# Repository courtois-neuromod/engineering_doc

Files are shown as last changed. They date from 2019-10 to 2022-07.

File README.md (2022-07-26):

# About
This document describes how to build the MR compatible videogame controller developed for the [Courtois Neuromod project](https://www.cneuromod.ca).

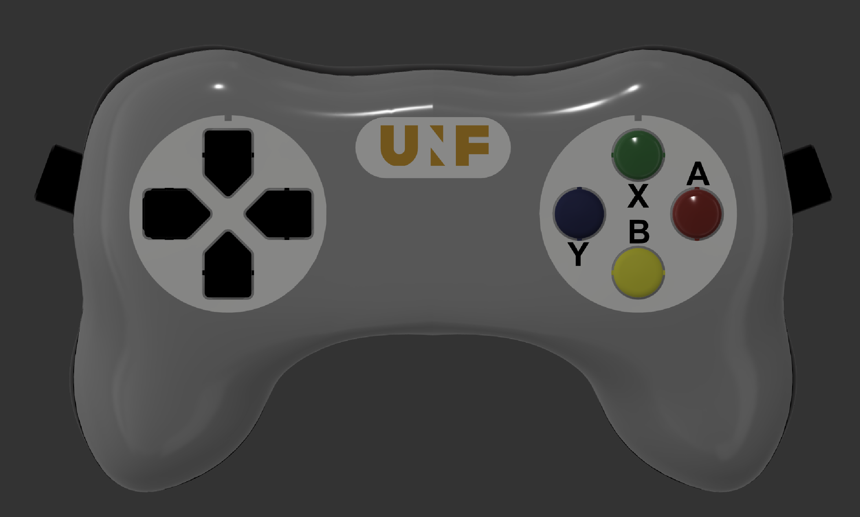
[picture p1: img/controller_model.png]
<br>
3D model of the controller design.

/!\ To add : overview schema of the different controller parts (i.e. body, fibers, PCB, stim computer)

## Documentation

- [Controller body assembly](https://github.com/courtois-neuromod/engineering_doc/blob/master/game_controller/controller_body/readme.md)
- [PCB electronics board](https://github.com/courtois-neuromod/engineering_doc/blob/master/game_controller/PCB/readme.md)
- [Software](https://github.com/courtois-neuromod/engineering_doc/tree/master/game_controller/teensy/source/readme.md)

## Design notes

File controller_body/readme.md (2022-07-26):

# Controller body instructions
This document describes the steps necessary to build and assemble the hand-held controller body part.

## Getting the parts
Aside from the 3D printed equipment and printed circuit boards, the parts required to build the controller can be obtained from two suppliers; [McMaster-Carr](http://mcmaster.com) and [Digikey](http://digikey.com). It is most likely possible to find other sources for the components, but the part numbers given here are for these two suppliers. The manufacturers names and part numbers are also given when available. The numbers given represent the bare minimum required to build the controller. Getting spares of everything is highly recommended.

## COTS
This section details the parts that need to be purchased directly from a supplier.
[BOM.md](BOM.md)

## Assembly

### Optical switches

#### Shutter assembly

Required:

Parts
  - Shutter_Blade x 8
  - Shutter_Cap x 8
  - Switch_Body x 8

Tools
  - Cyanoacrylate adhesive
  - Fine sanding paper or files
  - X-acto knife

Check both shutter blade and shutter cap for smoothness of surface and file or sand any rough surface. Test insertion of blade into slot at the bottom of shutter cap. It should slide to the bottom easily but you should still feel a bit of resistance. Put a drop of cyanoacrylate adhesive on a liquid tight surface, dip the end of shutter blade in adhesive and insert into slot at bottom of shutter cap.

Shutter assembly drawing | Shutter assembly exemple
---|---
Switch assembly exploded view |Switch assembly exploded view

#### Switch assembly

1. Disassemble a discarded computer keyboard to recuperate the membrane making the rubber dome switches. Individually cut away the switch dome parts and remove centre of top surface using an x-acto knife.

Silicone membrane

2. Test assembly of shutter, membrane and switch body by inserting the shutter by inserting the shutter blade into the empty centre part of rubber dome, then into gap at the top of switch body. The shutter blade should completely occult the guide hole for the fiber optic when button is pressed down, but leave it free when in upward position. The distance between the bottom
 of the shutter cap and the top of switch body will determine the stroke length of the key. The smaller this distance, the more responsive the controls will be. The shutter should move freely up and down.

 Air Gap Visual Check

 Shutter up | Shutter pressed down
 ---|---
 Shutter up |Shutter down

 3. Since the rubber domes recuperated from computer keyboards will very likely vary in dimensions, it might be necessary to modify shutter cap and shutter blade dimensions. The file [Shutter_Assembly_Param.f3d](CAD/f3d/Shutter_Assembly_Param.f3d) contains these two parts in Autodesk Fusion 360 format. The design is parametric to facilitate modifications. To edit the parts, open the file in **Fusion 360**, go to Modify, then select change parameters and expand User Parameters. Changing the value of parameter *Shutter_Cap_Shaft_Length* will allow to adjust the stroke length, while changing *Shutter_Blade_L* will allow ensuring correct shutter operation. That part is also available in [.step](/CAD/stp/Shutter_Cap.step) format for import in other CAD programs.

Parameters edit in Fusion 360<br>

4. Ensure that the air gap and the fiber optic guide in the 3D printed switch bodies are free of any residual PLA or support material. Hold switch body in front of a light source and check along Z axis for the air gap, and along horizontal axis for the fiber optic guide.

### Controller body

1. For each control on the controller, cut one length of duplex fiber optic to desired length between controller and interface module + 150 mm
2. Split each length of fiber on its length to separate the 2 fibers on a distance of approx. 750 mm from one end, and 25 mm from second end
3. Label each fiber with the name of matching control. On the end where the fibers are split for the largest distance (controller end) place a label on each single fiber
4. On the controller side of the fibers, make two bundles of fibers. Place one fiber of eac78h control in either bundle.
5. For one of the two bundles, cut the fibers for the directional pad controls about 150 mm shorter than the ones for the buttons. Do the opposite with the other bundle. This will allow a cleaner layout of the fibers inside the casing.
6. Strip and polish fibers **(need procedure)**
7. Cut two 500 mm lengths of the 13 mm ID plastic hose and fix those on the ends of the Y splitter
8. Fix second end of plastic hoses to extrusions on part *Casing_Bottom*

Fiber_Sheath_Assembly

Fiber_Sheath_Assembly

9. For each control, place a *Switch_Body* in matching groove inside casing.

Switch_Body_Positioning

10. Insert the fiber optics into Y splitter and push gently until both fibers emerge inside of casing. The bundle where the buttons fibers are longer will go on the directional pad side. There will be one fiber for each control in each branch of the Y. Make sure that the length protruding inside the casing is enough to reach into the corresponding *Switch_Module* and allow to lay out cleanly inside casing.
11. For each control, glue both fibers in place **(Need glue specs)**
12. Optional: Depending on fit tightness of *Switch_Module* parts inside grooves, it is also possible to glue the module in place. If gluing modules in place, wait for glue on fibers to set before proceeding
13. Place one threaded Nylon insert in each mounting post of part *Casing_Top*. If inserts don't fit inside, re-drill hole using 1/4" (6.35 mm) bit. If inserts are loose, use a drop of cyanoacrylate adhesive

Threaded_Inserts<br>

14. Before starting assembly, test bottom and top parts of casing for fit. The two halves should fit together without any visible gap. Common area that might need post processing are the top and bottom of screw posts and the lip that runs around the perimeter of the bottom part, as well as the matching flat surface on the top part. If necessary, file or sand away excess of material that might prevent case from closing properly.

<br>
Test casing for fit

 |<br>
Areas commonly requiring post-processing

### Optical fibers assembly
<br>
Parts ready for assembly

1. Separate bundle of fiber optics into two smaller bundles of 8 fibers each. Pull each smaller bundle through the Y splitter with one small bundle coming out of each of the Y branches. Pull each of the smaller bundle into the 1 meter protective sheath until there is approximately 300 mm of fibers coming out of each sheath.

<br>
Separating fibers bundle with Y splitter

2. Pull each bundle into the bottom part of casing through openings on the sides and make sure that the sheaths fit nicely on the protruding parts and that you have at least 200 mm length of fibers going into the casing on both sides.

<br>
Fibers insertion in casing

3. Strip fibers and polish the fibers. It's possible to use a regular wire stripping tool set for #18 wire size. Insert fibers into switch body so teh tip of the fiber is flush with the internal wall of the air gap. Ensure that the shutter is free to move after the fibers are in place.
4. Use a drop a glue to affix the fibers to the switch body. The type of glue is not critical, but **do not use** cyanoacrylate or other type of _permanent_ glue. These will work, but they will make the switch impossible to repair, which means in case of a broken fiber or other problem, you will need to replace the whole switch.

</br>

<br>
Fibers connections and testing

5. To assemble the switch inside the casing, it is easier to proceed by pairs, waiting for the glue on the fibers to set before proceeding to the next pair. Proceeding that way allows to move the fibers around to route them cleanly inside the casing without pulling them out from the body of already installed switches. The order is not critical, but it is a lot easier to finish with the pair that's the closest to the opening where the fibers enter the casing.

<br>
Assembling first pair of controls

<br>
Assembling second pair of controls

<br>
Assembling third pair of controls

<br>
Assembling fourth pair of controls

<br>
Add buttons supports

<br>
Installing rubber membranes and shutters

<br>
Finished view

<br>
Re-install buttons supports

<br>
Close casing

<br>
Casing closed top view

<br>
Install buttons

<br>
Finished view

<br>
Install direction pad cover and buttons cover

<br>
Assembly complete

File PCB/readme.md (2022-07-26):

# PCB assembly instructions
Get PCB 3D model [here](../CAD/stp/neuromod_game_controller_v1.zip)

## Ordering PCBs

Get Gerber files [here](GerberFiles.zip) and send to fab house

## Assembly
<br>
Raw PCB view

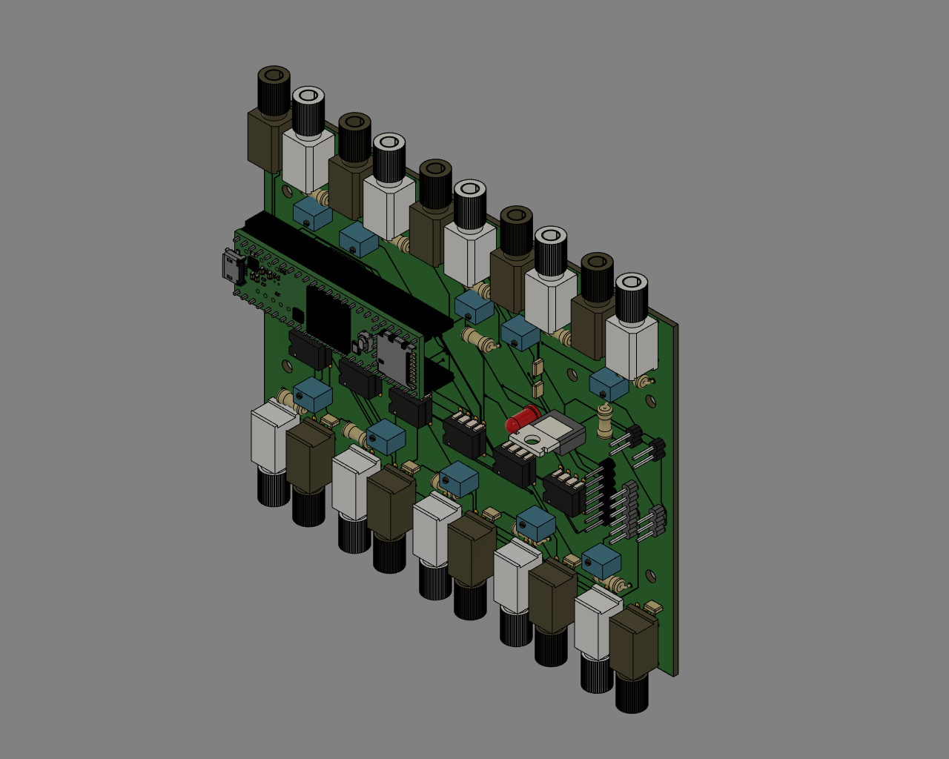
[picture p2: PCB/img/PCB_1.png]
<br>
PCB isometric view

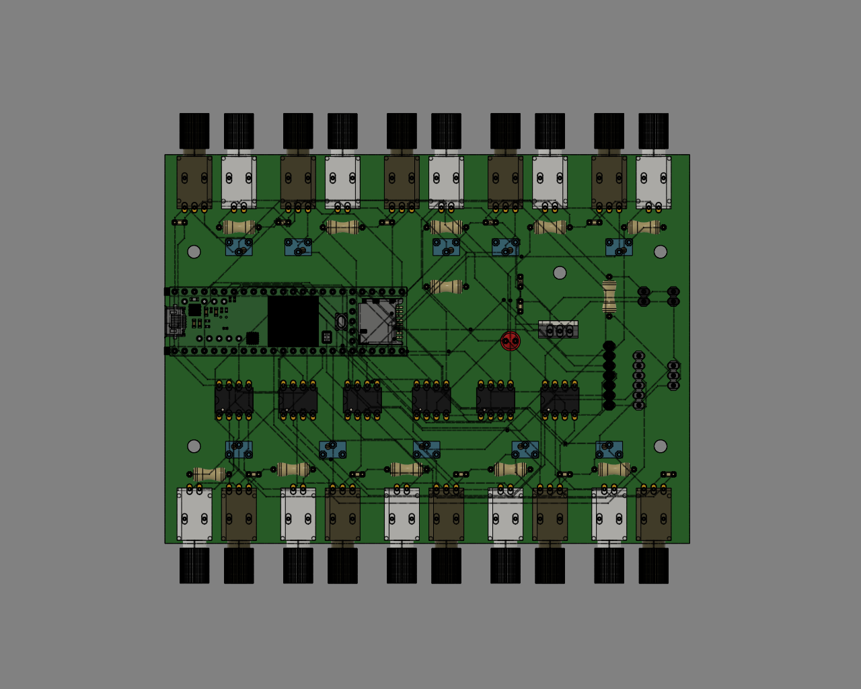
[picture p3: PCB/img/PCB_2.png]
<br>
PCB Top view

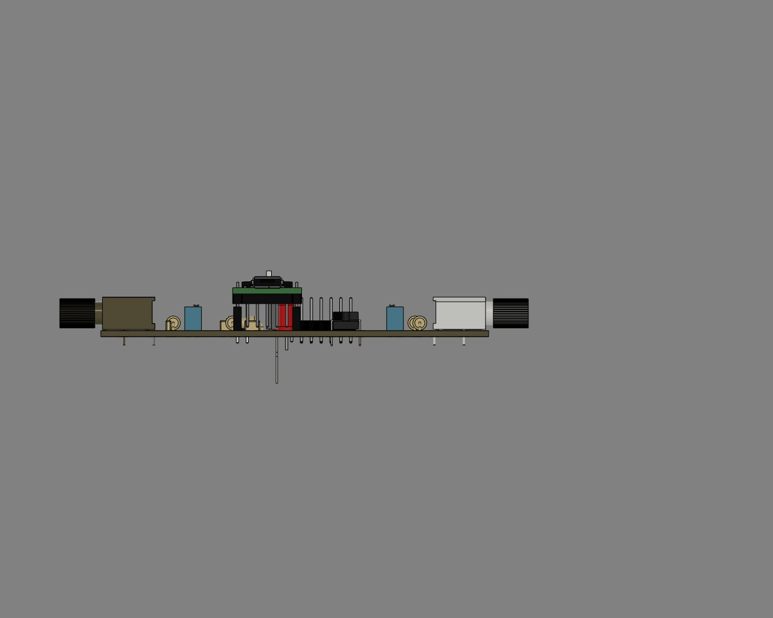
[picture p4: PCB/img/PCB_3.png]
<br>
PCB Side view

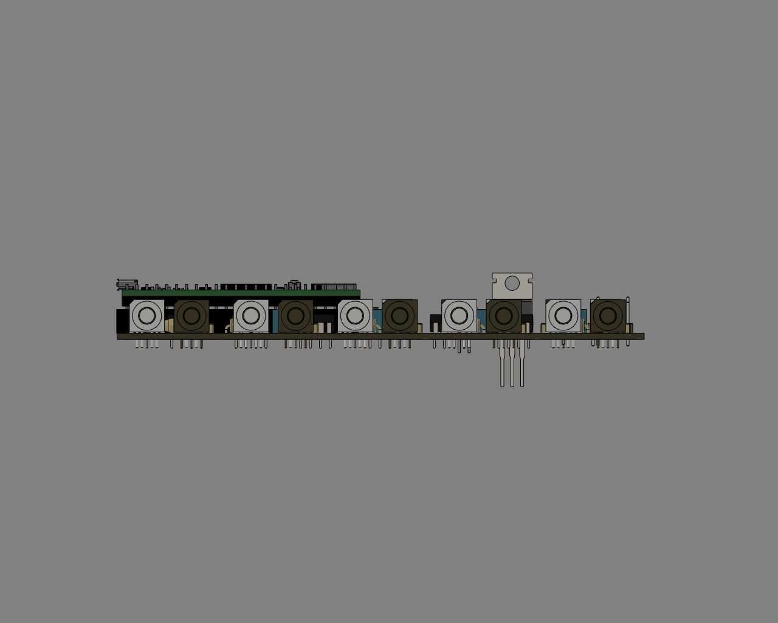
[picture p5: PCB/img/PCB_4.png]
<br>
PCB Side view

Teensy with headers | Teensy on PCB
---|---
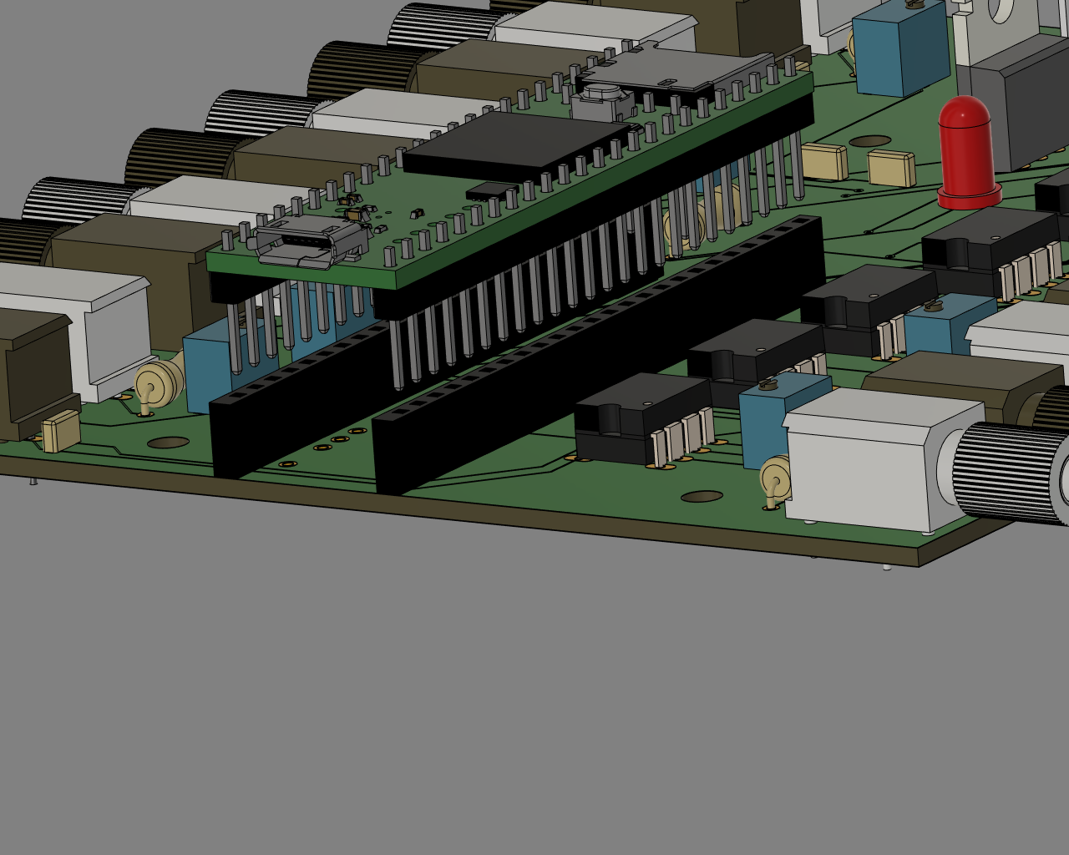
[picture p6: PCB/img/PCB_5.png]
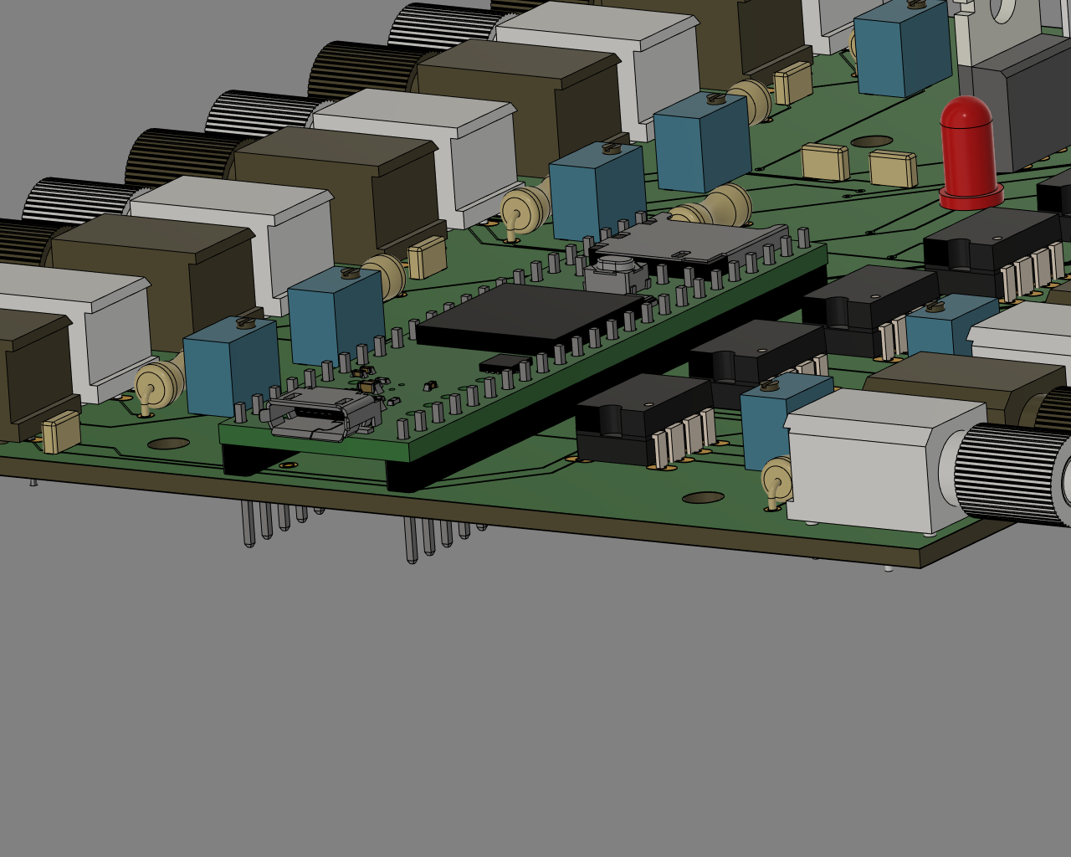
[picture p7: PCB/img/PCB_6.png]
 |

The Teensy board can be mounted either on headers (left) or directly on PCB (right). The first option is recommended as is allows easy replacement in case of damage.

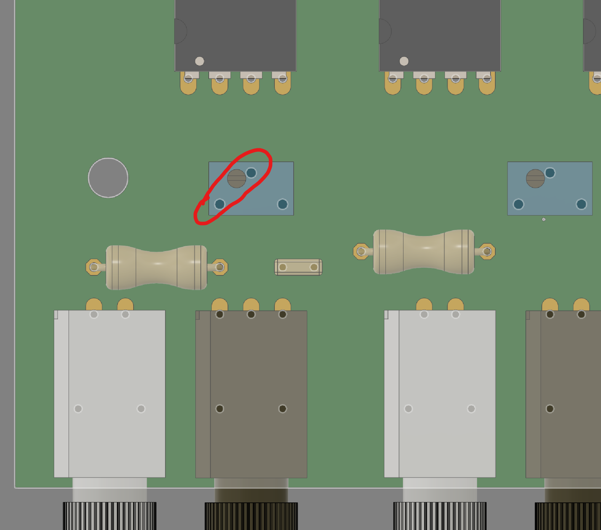
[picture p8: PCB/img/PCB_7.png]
<br>
Adjust potentiometer to be 330 Ω between the two illustrated pins or solder directly a 330 Ω resistor between those pins.

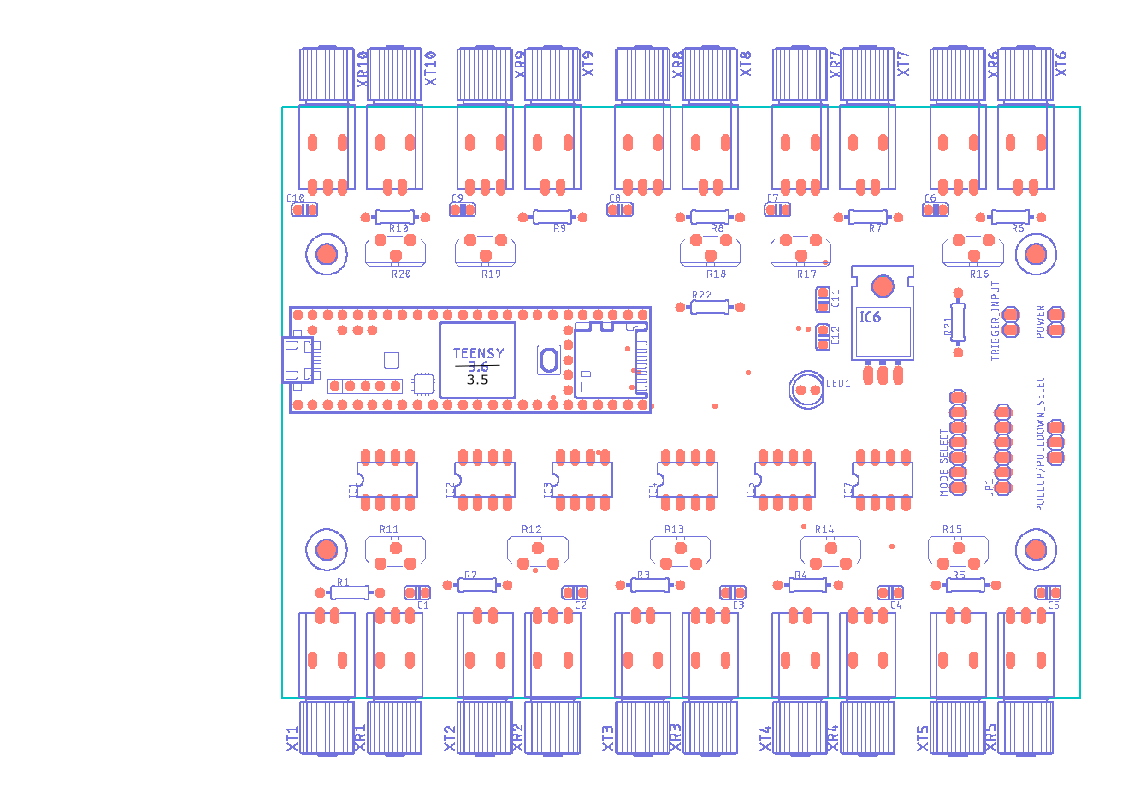
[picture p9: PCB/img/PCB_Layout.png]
<br>
Board layout

Schematics | Component| Value
-----------|----------|---|
IC1 - IC5, IC7|Gate driver|SN75451BP
IC6|Voltage regulator|LM340
R1 - R10|Resistor| 65 Ω
R11 - R29|Resistor|330 Ω between pin 1 & 3
R21|Resistor| 5 kΩ
C1 - C8|Capacitor|0.1 µF
C11,C12|Capacitor|10 µF
TX1 - TX10|Fiber optic transmitter|SFH756V
RX1 - RX10|Fiber optic receiver|SFH551V
Teensy 3.5 | Use version 3.5 **NOT 3.6**

TX9,TX10,RX9,RX10 and associated components are optional. They were meant for additional controls not implemented on this version of the controller. They can also be used for troubleshooting purpose or to fix a damaged channel.

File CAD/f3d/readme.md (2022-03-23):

This folder contains native CAD files for the project. The controller was designed with Autodesk Fusion 360.

List of files:

- [Controller assembly](Videogame_Controller_V5.f3z)
- [Parametric design for the shutter part](Shutter_Assembly_Param v1.f3d)

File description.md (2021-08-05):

# Intro

# Design considerations

## MR/MEG compatibility

## Performance

# Description

## Mechanical

### Enclosure
The enclosure for the controller is the part that will be held by the participant inside the MR scanner. It has to be free of any metallic/electronic part. It was designed using Autodesk Fusion 360, basing the model on the general shape of different commercially available controllers. All parts were 3D printed using an Ultimaker 3 printer with PLA filament.  
The top and bottom parts of the casing are held together with commercially available Nylon 6/6 threaded inserts and polycarbonate screws.

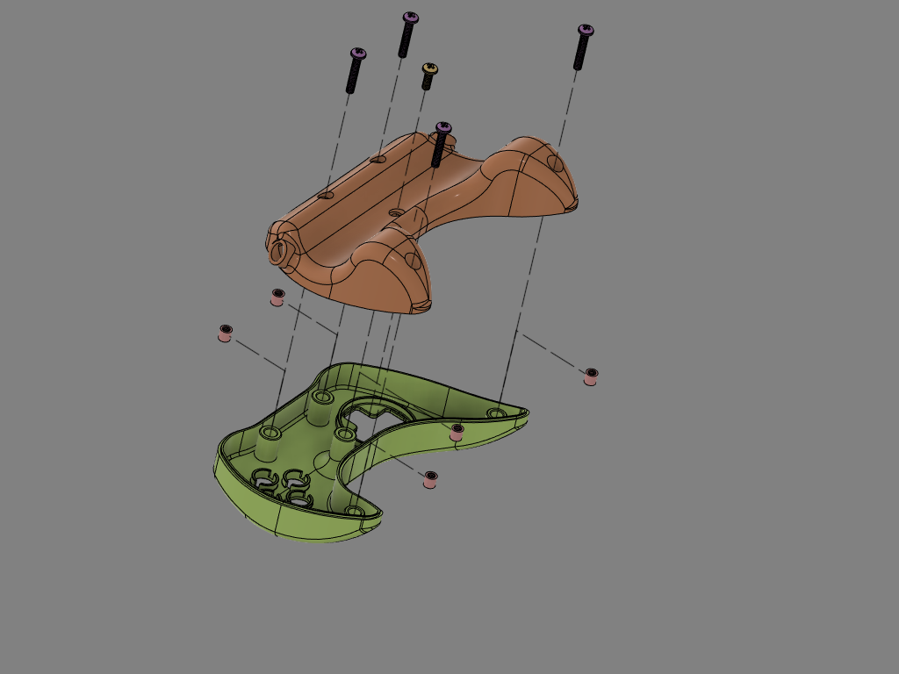
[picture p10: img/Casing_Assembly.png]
Casing assembly
</br>
**_Casing assembly_**

### Switch mechanism
The sensing mechanism for all controls is made of 2 optical fibers of 10 m length going from the electronics interface in the scanner control room to the enclosure inside the scanner and back. Inside the enclosure, the transmitting and receiving fibers are aligned by insertion in a switch module and positioned facing each other leaving a 0.8 mm air gap. When a button is pressed, a small shutter blade moves down to block the light going through and the optical receiver module located in the control room triggers a digital input on the microcontroller.

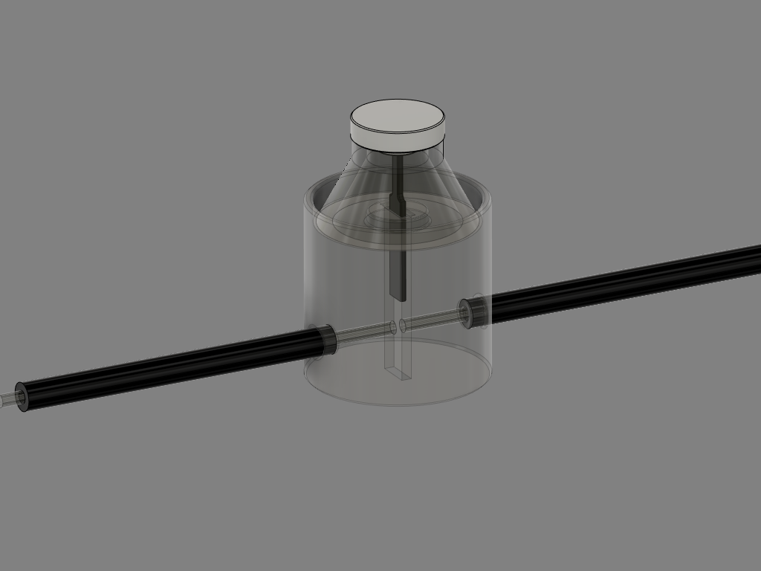
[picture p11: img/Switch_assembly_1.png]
Switch assembly
</br>
**_Optical switch_**

## Electronics

### Fiber emitter
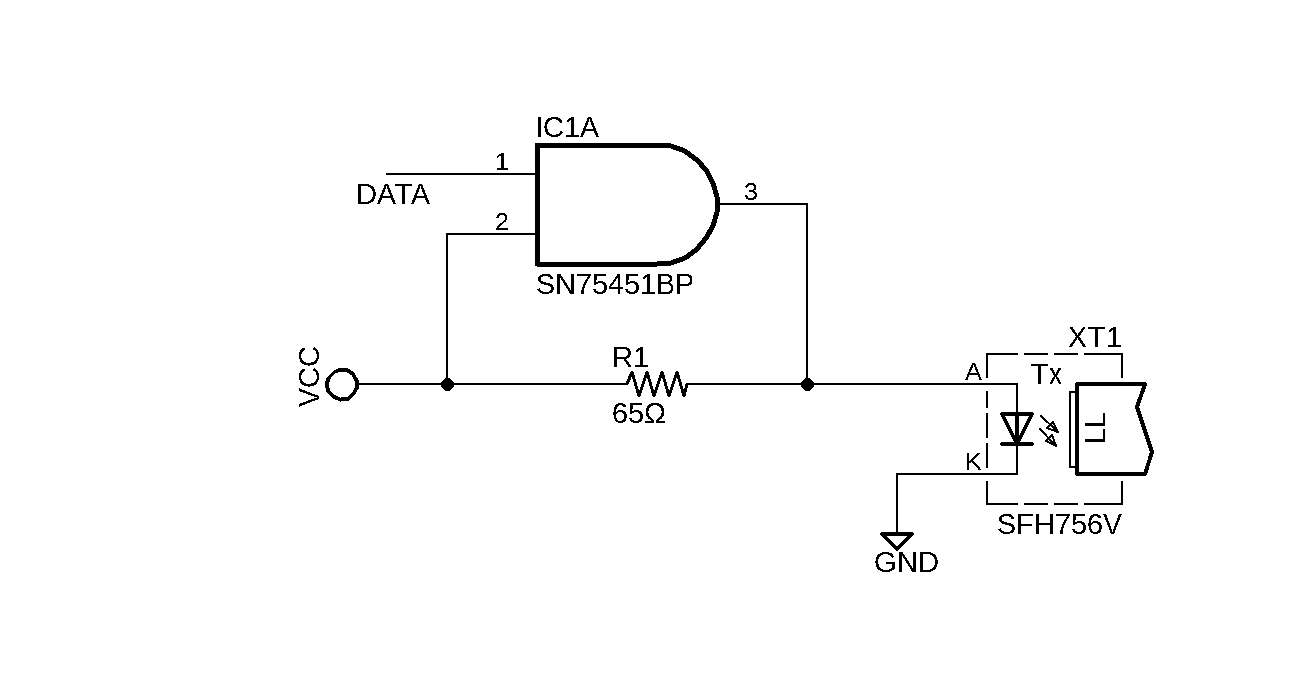
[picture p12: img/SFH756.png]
Fiber optic transmitter


### Fiber receiver
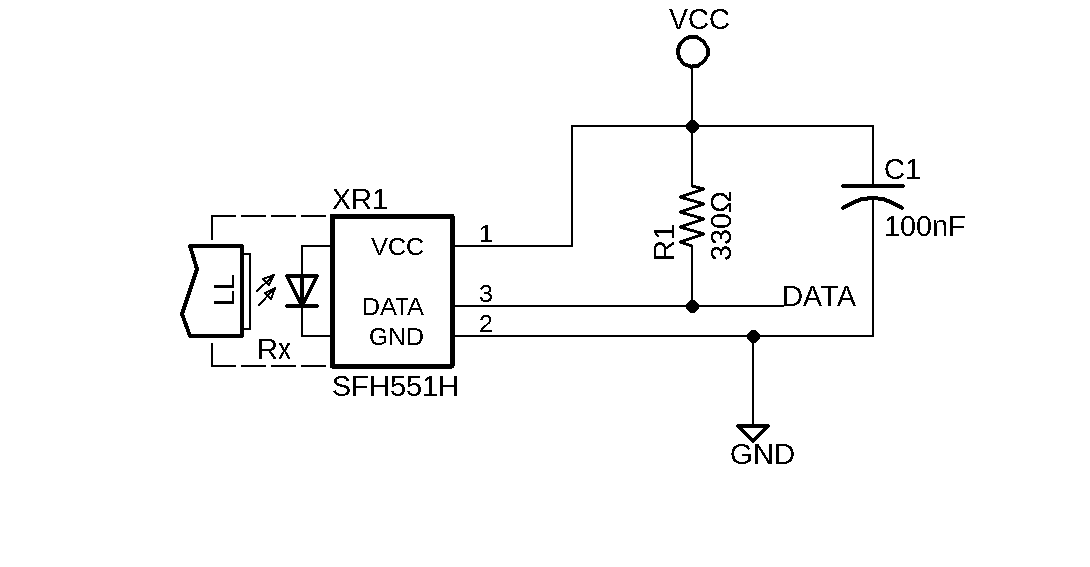
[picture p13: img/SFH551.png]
Fiber optic receiver


## Programming

# Construction

Suppliers used:  
- Digikey Electronics [www.digikey.com](www.digikey.com)  
- McMaster-Carr [www.mcmaster.com](www.mcmaster.com)

Part | Manufacturer | Supplier | Manufacturer part no. | Supplier part no. | Qty
-----|--------------|----------|-----------------------|------------------|-|
Fiber optic cable | Broadcom Limited | Digikey | HFBR-RUD500Z | 516-2094-ND | 1
Fiber optic transmitter | Broadcom Limited | Digikey | SP000063814 | 516-2213-ND | 10
Fiber optic receiver | Broadcom Limited | Digikey | SP000063855 | 516-2455-ND | 10
Teensy 3.5 microcontroller board | SparkFun Electronics | Digikey |DEV-14055 |1568-1443-ND | 1
Gate driver | Texas Instruments | Digikey | SN75451BP | 	296-1746-5-ND | 5
Hose 13mm ID, black PE|Panduit Corp|Digikey|CLTS50F-C|298-13576-ND | 1
Hose 19.48mm ID, black PE|Panduit Corp|Digikey|CLTS75F-C|	298-13577-ND | 1
Resistor 330 Ω | | Digikey | | 	A131459CT-ND | 10
Polycarbonate Pan Head Philips Screw 8-32 x 1" | | McMaster-Carr| |93140A782 | 2
Polycarbonate Pan Head Philips Screw 8-32 x 1/2" | | McMaster-Carr | |93140A588 | 3
Nylon 6/6 Female Threaded Round Standoff 8-32 x 1/4"| | McMaster-Carr| |96110A026 | 5

Other:
- Silicone membrane from discarded computer keyboard

# Mechanical

## Required
- CAD Software
- Slicing software
- Access to 3D printer

### CAD
All parts were designed using Autodesk Fusion 360.

## 3D printing parts
All 3D printed parts were printed on a Ultimaker 3 printer (Ultimaker) using PLA or ABS plastic.

Part | Qty needed | Material 1 | Material 2 | Nozzle 1 size | Nozzle 2 size | Layer height | Print direction
----|------------|------------|---------------|---------------|--------------|---------------|--|
Casing_Top | 1 | PLA | PVA | 0.4 mm | 0.4 mm | 0.2 mm | +Y
Casing_Bottom | 1 | PLA | PVA | 0.4 mm | 0.4 mm | 0.2 mm | -Y
Switch_Body | 8 |PLA | - | 0.25 mm | - | 0.1 mm | +Y
Shutter_Blade | 8 |PLA | - | 0.25 mm | - | 0.06 mm | +Z
Shutter_Cap | 8 | PLA | - | 0.25 mm | - | 0.06 mm | -Y
Button_Cap | 4 | PLA | PVA | 0.25 mm | 0.4 mm | 0.1 mm | +Y
DPad_Support | 1 | PLA | PVA | 0.4 mm | 0.4 mm | 0.1 mm | +Y
DPad_Cross | 1 | PLA | PVA | 0.4 mm | 0.4 mm | 0.1 mm | +Y

Main 3D printing parameters

## Silicone membranes
Use sharp Xacto knife to cut free the silicone dome used to push the keys upward after a keystroke. Carefully cut away the center of the top part to leave hole for shutter.
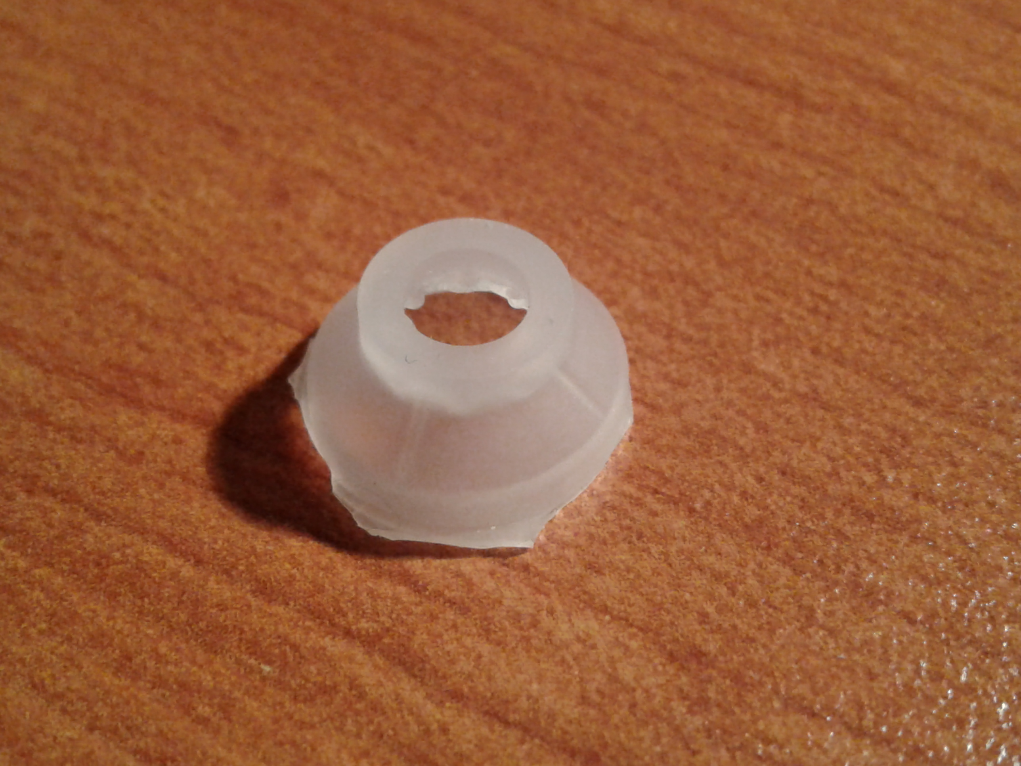
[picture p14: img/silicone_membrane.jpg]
Silicone membrane


## Assembly

### Interface enclosure

# Electronics

## Obtaining interface printed circuit board

List of gerber files needed

## Assembling circuit

# Software

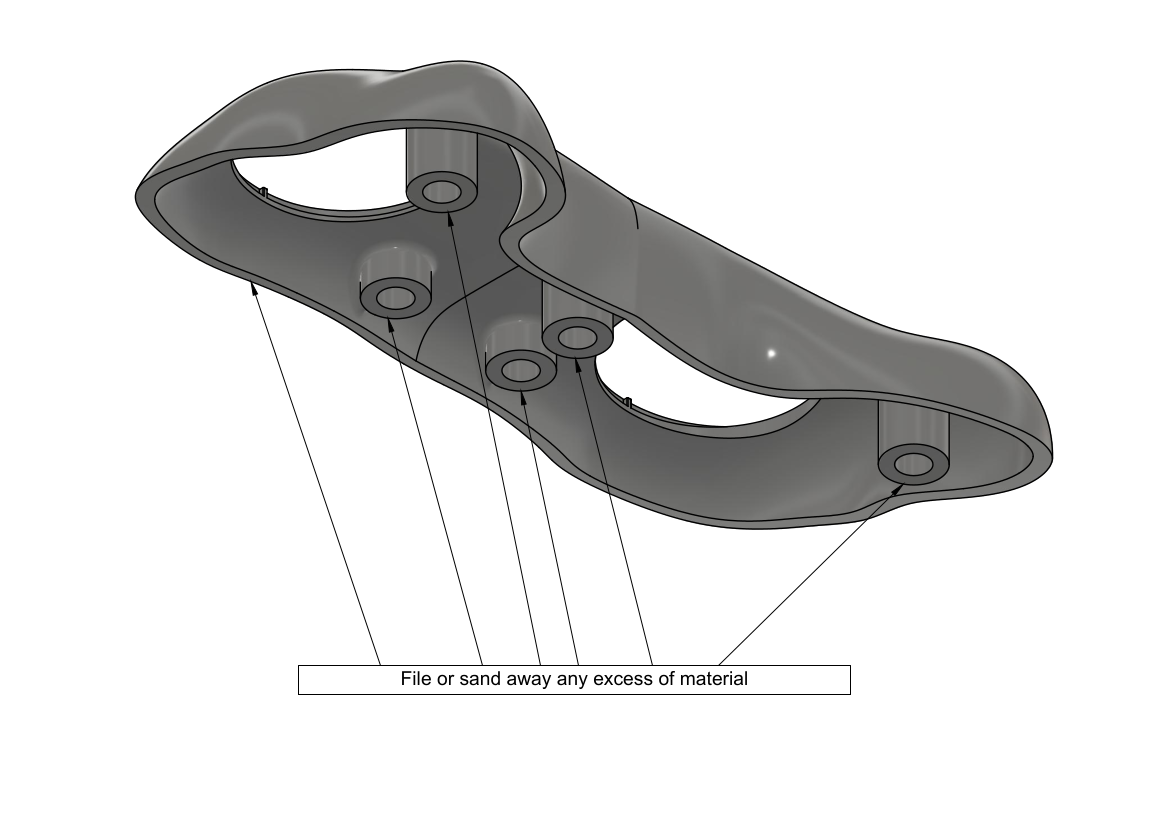
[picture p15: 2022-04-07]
img/PostProcess_Top.png

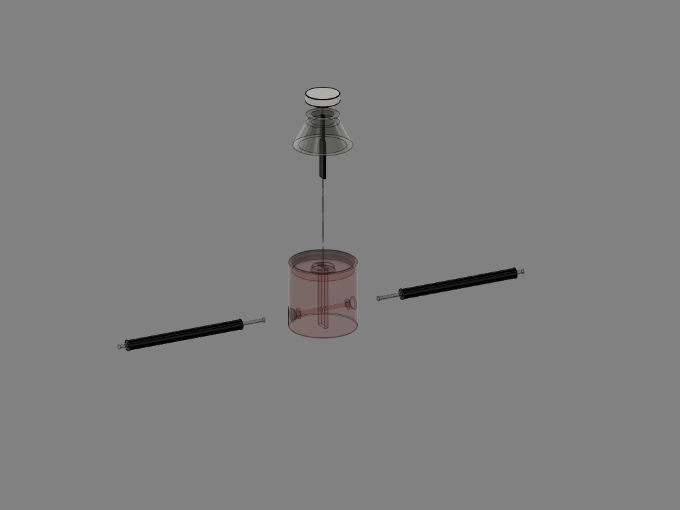
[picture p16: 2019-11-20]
img/Switch_exploded.png

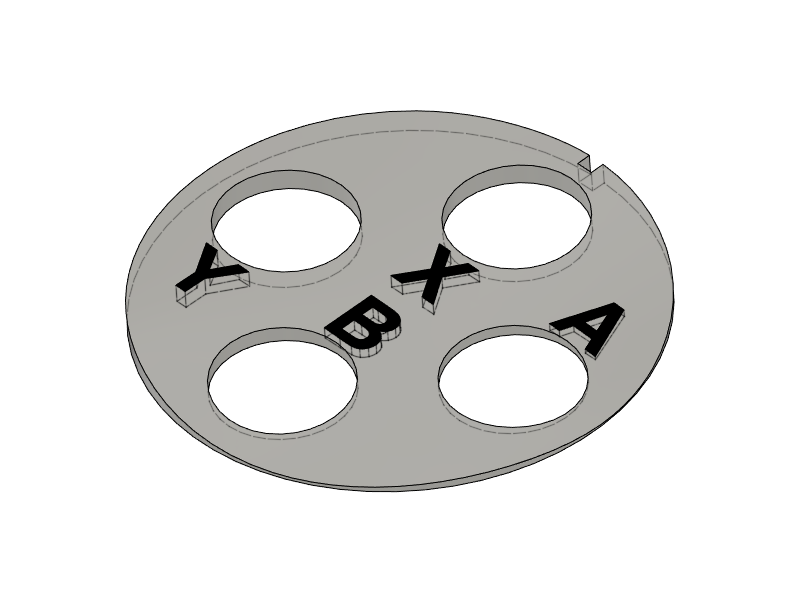
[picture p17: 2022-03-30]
img/Button_Cover.png

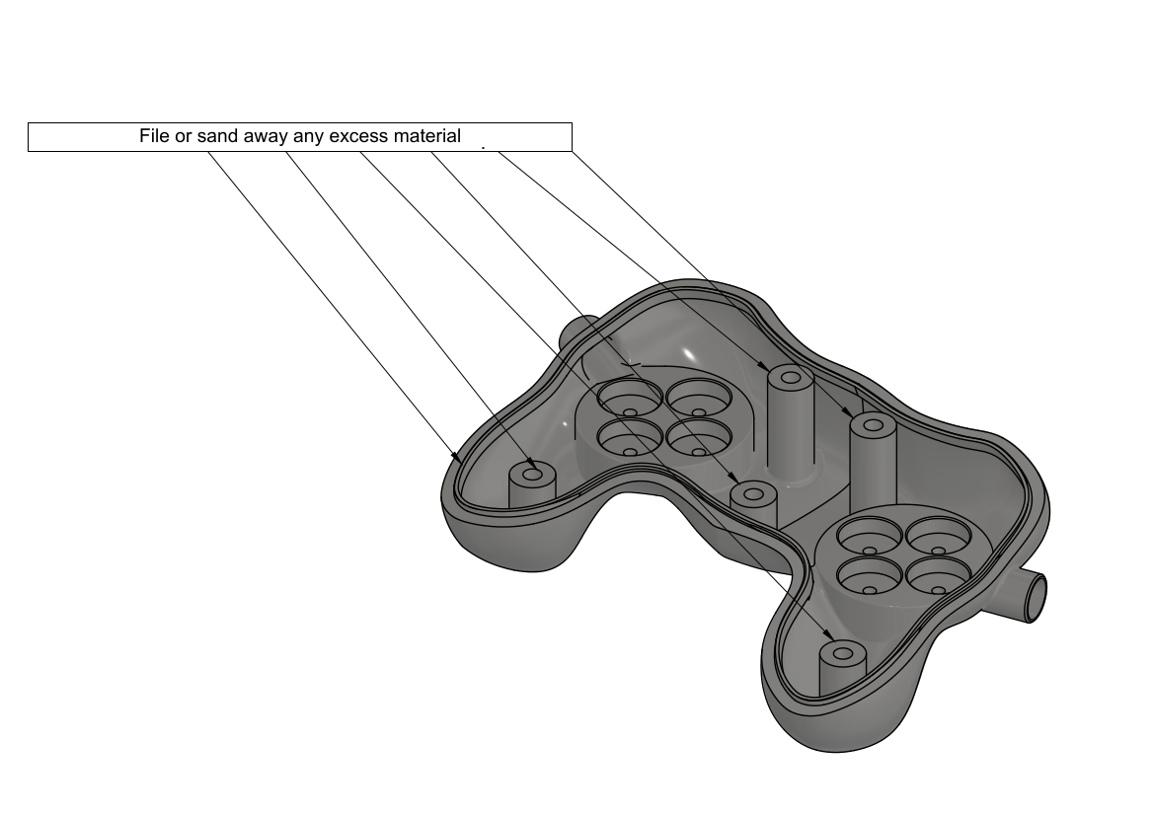
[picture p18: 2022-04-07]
img/PostProcess_Bottom.png

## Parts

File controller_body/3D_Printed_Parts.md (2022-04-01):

This file details the list of 3D printed parts required to build the controller and gives information about the main printing parameters used. All parts were printed using an Ultimaker 3 [http://ultimaker.com](http://ultimaker.com) printer. The print direction given was set as the positive Z direction in the printer. So if the direction **+Y** is given, the positive Y direction from the .stl file was set as positive Z () in the slicing software.

Parts usually require a small amount of post finishing. A kit of fine grit files like https://www.mcmaster.com/8174A42/ is very useful for that purpose.

## List of files

1. [Casing_Top](CAD/stl/Top.zip)
2. [Casing_Bottom](CAD/stl/Bottom.zip)
3. [Switch_Body](CAD/stl/Switch_Body.zip)
4. [Shutter_Cap](CAD/stl/Shutter_cap.zip)
5. [Shutter_Blade](CAD/stl/Shutter_Blade.zip)
6. [DPad_Support](CAD/stl/DPad_Support.zip)
7. [Dir_Button](CAD/stl/Dir_Button.zip)
8. [Button_Cap](CAD/stl/Button_Cap.zip)
9. [DPad_Cover](CAD/stl/DPad_Cover.zip)
10. [Button_Cover](CAD/stl/Buttons_Cover.zip)
11. Y_Splitter
12. [Interface_Casing_Top](CAD/stl/Interface_Top.zip)
13. [Interface_Casing_Bottom](CAD/stl/Interface_Bottom.zip)
14. Fiber_Cutting_Block

## Casing top
[Top.zip](CAD/stl/Top.zip) | Casing Top
------|--------
Weight|53.8 g
Volume|46.4 cm<sup>3</sup>
Bounding box | 155.4 x 43.5 x 94.9 mm
Qty | 1
Material 1 | PLA
Material 2 (support) | PVA
Material 1 density | 100%
Material 2 density | 40%
Nozzle 1 size | 0.8 mm
Nozzle 2 size | 0.4 mm
Nozzle 1 temperature | 205 °C
Nozzle 2 temperature | 230 °C
Bed temperature | 50 °C
Layer height | 0.15 mm
Print direction | +Y
Comments

## Casing bottom
[Bottom.zip](CAD/stl/Bottom.zip) | Casing Bottom
------|--------
Weight|107.9 g
Volume|87.0 cm<sup>3</sup>
Bounding box | 169.8 x 58.8 x 95.1 mm
Qty | 1
Material 1 | PLA
Material 2 (support) | PVA
Material 1 density | 100%
Material 2 density | 40%
Nozzle 1 size | 0.8 mm
Nozzle 2 size | 0.4 mm
Nozzle 1 temperature | 205 °C
Nozzle 2 temperature | 230 °C
Bed temperature | 50 °C
Layer height | 0.15 mm
Print direction | -Y
Comments

## Switch body
[Switch_Body.zip](CAD/stl/Switch_Body.zip) | Switch Body
------|--------
Weight|3.6 g
Volume|2.9 cm<sup>3</sup>
Bounding box | 16.0 x 18.5  x 16.0 mm
Qty | 8
Material 1 | PLA
Material 2 (support) | same as material 1
Material 1 density | 100%
Material 2 density | 40%
Nozzle 1 size | 0.25 mm
Nozzle 2 size | N/A
Nozzle 1 temperature | 205 °C
Nozzle 2 temperature | N/A
Bed temperature | 50 °C
Layer height | 0.1 mm
Print direction | +Y
Comments|

## Shutter cap
[Shutter_Cap.zip](CAD/stl/Shutter_cap.zip) | Shutter Cap
------|--------
Weight|0.19 g
Volume|0.15 cm<sup>3</sup>
Bounding box | 7.5 x 6.3  x 7.5 mm
Qty | 8
Material 1 | PLA
Material 2 (support) | -
Material 1 density | 100%
Material 2 density | -
Nozzle 1 size | 0.25 mm
Nozzle 2 size | -
Nozzle 1 temperature | 205 °C
Nozzle 2 temperature | -
Bed temperature | 50 °C
Layer height | 0.1 mm
Print direction | -Y
Comments|

## Shutter blade
[Shutter_Blade.zip](CAD/stl/Shutter_Blade.zip) | Shutter Blade
------|--------
Weight|0.014 g
Volume|0.0012 cm<sup>3</sup>
Bounding box | 0.5 x 11.7 x 2.2 mm
Qty | 8
Material 1 | PLA
Material 2 (support) | -
Material 1 density | 100%
Material 2 density | -
Nozzle 1 size | 0.25 mm
Nozzle 2 size | -
Nozzle 1 temperature | 205 °C
Nozzle 2 temperature | -
Bed temperature | 50 °C
Layer height | 0.06 mm
Print direction | +X
Comments | This works better if printed with dark (ideally black) material. This part takes very little material, prints fast and warps easily, so print lots of it and keep the best ones.

## Direction pad support
[DPad_Support.zip](CAD/stl/DPad_Support.zip) | Directional Pad Support
------|--------
Weight|14.6 g
Volume|11.8 cm<sup>3</sup>
Bounding box | 46.9 x 13.2  x 48.5 mm
Qty | 14
Material 1 | PLA
Material 2 (support) | PVA
Material 1 density | 100%
Material 2 density | 30%
Nozzle 1 size | 0.4 mm
Nozzle 2 size | 0.4 mm
Nozzle 1 temperature | 205 °C
Nozzle 2 temperature | 230 °C
Bed temperature | 50 °C
Layer height | 0.1 mm
Print direction | +Y
Comments | Some post finishing of guiding slots may be required to get smooth button motion. Use of fine grit small detailing files or sanding paper recommended. This part can be printed at lower density than 100%, but make sure that walls are thick enough. Cura's default with 0.4 mm nozzle is 1 mm. At least double that.

## Button support
[Buttons_Support.zip](CAD/stl/Buttons_Support.zip) | Directional Pad Support
------|--------
Weight|16.0  g
Volume|12.9 cm<sup>3</sup>
Bounding box | 46.9 x 13.2  x 48.5 mm
Qty | 1
Material 1 | PLA
Material 2 (support) | PVA
Material 1 density | 100%
Material 2 density | 30%
Nozzle 1 size | 0.4 mm
Nozzle 2 size | 0.4 mm
Nozzle 1 temperature | 205 °C
Nozzle 2 temperature | 230 °C
Bed temperature | 50 °C
Layer height | 0.1 mm
Print direction | +Y
Comments | Some post finishing of guiding slots may be required to get smooth button motion. Use of fine grit small detailing files or sanding paper recommended. This part can be printed at lower density than 100%, but make sure that walls are thick enough. Cura's default with 0.4 mm nozzle is 1 mm. At least double that.

## Direction button
[Dir_Button.zip](CAD/stl/Dir_Button.zip) | Direction_Button
------|--------
Weight|1.6 g
Volume|1.3 cm<sup>3</sup>
Bounding box | 14.0 x 12.0  x 13.0 mm
Qty | 4
Material 1 | PLA
Material 2 (support) | PVA
Material 1 density | 100%
Material 2 density | 30%
Nozzle 1 size | 0.25 mm
Nozzle 2 size | 0.4 mm
Nozzle 1 temperature | 205 °C
Nozzle 2 temperature | 230 °C
Bed temperature | 50 °C
Layer height | 0.06 mm
Print direction | +Y
Comments | Precision of dimensions and finish quality are very important for this part. Fill percentage does not really matter, but this is a very small part, so material quantity and print time are both are not a problem.

## Round button
[Button_Cap.zip](CAD/stl/Button_Cap.zip) | Round_Button
------|--------
Weight|1.19 g
Volume|0.96 cm<sup>3</sup>
Bounding box | 10.65 x 13.0  x 13.5 mm
Qty | 4
Material 1 | PLA
Material 2 (support) | PVA
Material 1 density | 100%
Material 2 density | 30%
Nozzle 1 size | 0.25 mm
Nozzle 2 size | 0.4 mm
Nozzle 1 temperature | 205 °C
Nozzle 2 temperature | 230 °C
Bed temperature | 50 °C
Layer height | 0.06 mm
Print direction | +Y
Comments | Precision of dimensions and finish quality are very important for this part. Fill percentage does not really matter, but this is a very small part, so material quantity and print time are both are not a problem.

## Direction pad cover
[DPad_Cover.zip](CAD/stl/DPad_Cover.zip) | DPad_Cover
------|--------
Weight|1.19 g
Volume|0.96 cm<sup>3</sup>
Bounding box | 10.65 x 13.0  x 13.5 mm
Qty | 4
Material 1 | PLA
Material 2 (support) | PVA
Material 1 density | 100%
Material 2 density | 30%
Nozzle 1 size | 0.25 mm
Nozzle 2 size | 0.4 mm
Nozzle 1 temperature | 205 °C
Nozzle 2 temperature | 230 °C
Bed temperature | 50 °C
Layer height | 0.06 mm
Print direction | +Y
Comments |

## Button_Cover
[Button_Cover.zip](/CAD/stl/Button_Cover.zip) | Button_Cover
------|--------
Weight|1.19 g
Volume|0.96 cm<sup>3</sup>
Bounding box | 10.65 x 13.0  x 13.5 mm
Qty | 4
Material 1 | PLA
Material 2 (support) | PVA
Material 1 density | 100%
Material 2 density | 30%
Nozzle 1 size | 0.25 mm
Nozzle 2 size | 0.4 mm
Nozzle 1 temperature | 205 °C
Nozzle 2 temperature | 230 °C
Bed temperature | 50 °C
Layer height | 0.06 mm
Print direction | +Y
Comments | This part uses 2 colors printing for the markings. You need to load 5 stl files in your slicer, assign each to the appropriate material, then merge them into one piece

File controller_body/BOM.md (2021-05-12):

# Bill of materials
Prices in Canadian dollars (May 2021)

Part | Manufacturer | Supplier | Manufacturer part no. | Supplier part no. | Price | Qty
-----|--------------|----------|-----------------------|-------------------|-------|-
**Electronics**
Fiber optic cable duplex 100m | Broadcom Limited | Digikey | HFBR-RUD100Z | [516-2093-ND](https://www.digikey.ca/en/products/detail/broadcom-limited/HFBR-RUD100Z/1990491) | $227.79 | 1
Fiber optic transmitter | Broadcom Limited | Digikey | SP000063814 | [516-2213-ND](https://www.digikey.ca/en/products/base-product/broadcom-limited/516/SP000063814/298985) | $18.60 | 8
Fiber optic receiver | Broadcom Limited | Digikey | SP000063855 | [516-2455-ND](https://www.digikey.ca/en/products/base-product/broadcom-limited/516/SP000063855/298987) | $22.62 | 8
Teensy 3.5 microcontroller board | SparkFun Electronics <sup>1</sup>  | Digikey |DEV-14055 | [1568-1443-ND](https://www.digikey.ca/en/products/detail/sparkfun-electronics/DEV-14055/6235191) | $33.67 | 1
Gate driver | Texas Instruments | Digikey | SN75451BP | [296-1746-5-ND](https://www.digikey.ca/en/products/detail/texas-instruments/SN75451BP/277392) | $1.34 | 5
Hose 13mm ID, black PE <sup>2</sup>|Panduit Corp|Digikey|CLTS50F-C|[298-13576-ND](https://www.digikey.ca/en/products/detail/panduit-corp/CLTS50F-C/4567741) | $86.41 | 1
Hose 19.48mm ID, black PE <sup>2</sup>|Panduit Corp|Digikey|CLTS75F-C|	[298-13577-ND](https://www.digikey.ca/en/products/detail/panduit-corp/CLTS75F-C/4567748) | $124.21 | 1
Voltage regulator | Texas Instruments  | Digikey |LM7805CT/NOPB | [296-47192-ND](https://www.digikey.ca/en/products/detail/texas-instruments/LM7805CT-NOPB/3901929) | $2.33 | 1
Resistor 330 Ω | TE Connectivity Passive Products | Digikey | ROX1SJ330R | 	[A131459CT-ND](https://www.digikey.ca/en/products/detail/te-connectivity-passive-product/ROX1SJ330R/8603589) | $0.42 | 8 |
Resistor 65 Ω | Vishay Beyschlag/Draloric/BC Components | Digikey | SFR16S0006499FR500 | 	[PPC64.9XCT-ND](https://www.digikey.ca/en/products/detail/vishay-beyschlag-draloric-bc-components/SFR16S0006499FR500/594439) | $0.25 | 8 |
Capacitor ceramic 0.1 µF | KEMET | Digikey | C315C104M5U5TA | 	[399-4151-ND](https://www.digikey.ca/en/products/detail/kemet/C315C104M5U5TA/817927) | $0.31 | 8 |
Capacitor ceramic 10 µF | KEMET | Digikey | C324C106K3R5TA | 	[399-13950-ND](https://www.digikey.ca/en/products/detail/kemet/C324C106K3R5TA/6562361) | $1.17 | 2 |
Connector header pin breakaway 24 pos |TE Connectivity AMP Connectors | Digikey | 4-102972-0-24 | 	[A26519-24-ND](https://www.digikey.ca/en/products/detail/te-connectivity-amp-connectors/4-102972-0-24/683577) | $3.32 | 4 |
Connector receptacle 24 pos |3M | Digikey | 929850-01-24-RA | 	[929850E-01-24-ND](https://www.digikey.ca/en/products/detail/3m/929850-01-24-RA/1094205) | $4.07 | 2 |
**Hardware**
Polycarbonate Pan Head Philips Screw 8-32 x 1" <sup>3</sup>| | McMaster-Carr| |[93140A782](https://www.mcmaster.com/93140A782) | $16.49 / pack of 25| 2
Polycarbonate Pan Head Philips Screw 8-32 x 1/2" <sup>3</sup>| | McMaster-Carr | |[93140A588](https://www.mcmaster.com/93140A588) | $16.49 / pack of 25| 3
Polycarbonate Pan Head Philips Screw 4-40 x 3/16" <sup>4</sup>| | McMaster-Carr | | [93140A403](https://www.mcmaster.com/93140A403)| $19.09 / pack of 50| 8
Nylon 6/6 Female Threaded Round Standoff 8-32 x 1/4" <sup>3</sup>| | McMaster-Carr| |[96110A026](https://www.mcmaster.com/96110A026) | $1.48| 5
Nylon 6/6 Female Threaded Round Standoff 4-40 x 1/8"| | McMaster-Carr| |[96110A001](https://www.mcmaster.com/96110A001) | $1.71| 8

1 : Actual manufacturer is [PJRC](https://www.pjrc.com/). SparkFun is Digikey's supplier
2 : Optional
3 : Metric equivalent M4 thread
4 : Metric equivalent M2.5 thread

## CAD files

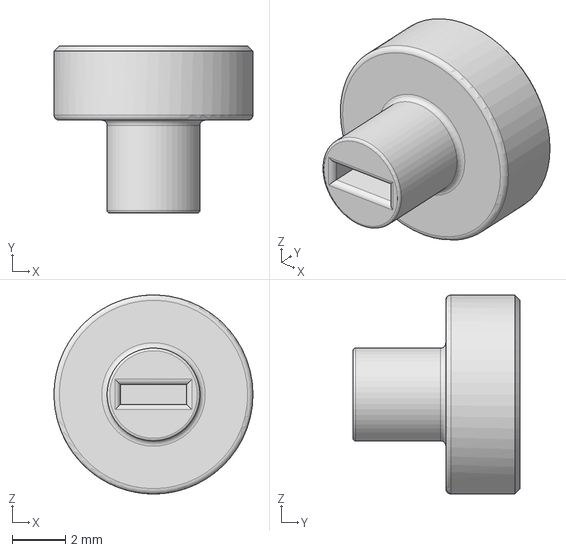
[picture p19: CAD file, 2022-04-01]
CAD/stp/Shutter_Cap.step
7.50 x 6.30 x 7.50 mm

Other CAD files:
CAD/f3d/Shutter_Assembly_Param.f3d

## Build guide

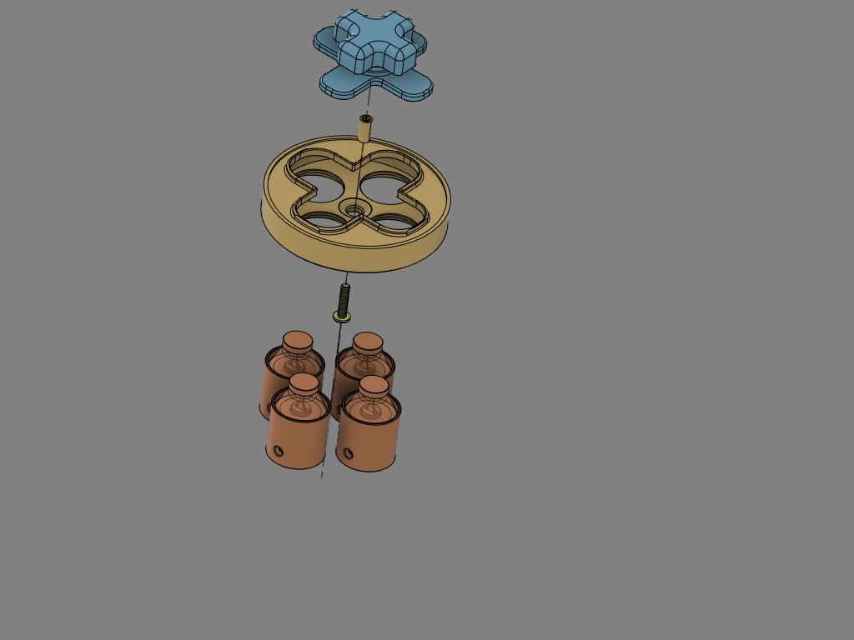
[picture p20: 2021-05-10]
img/DPad_assembly.png

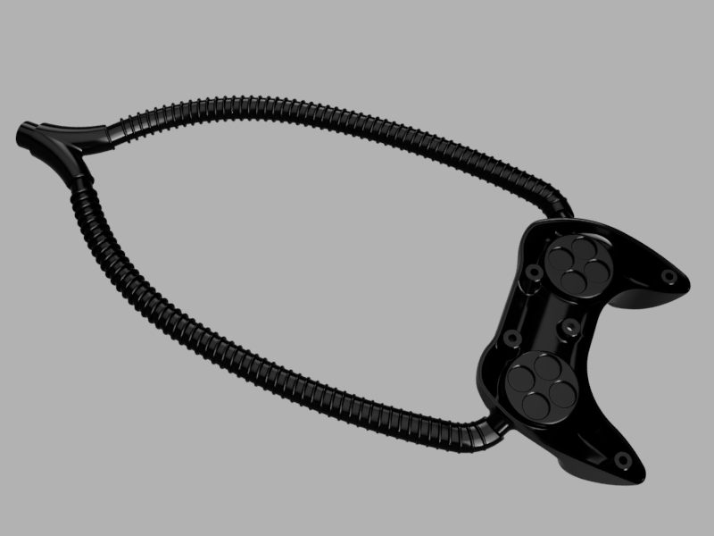
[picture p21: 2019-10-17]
img/Fiber_Sheath_Assembly.png

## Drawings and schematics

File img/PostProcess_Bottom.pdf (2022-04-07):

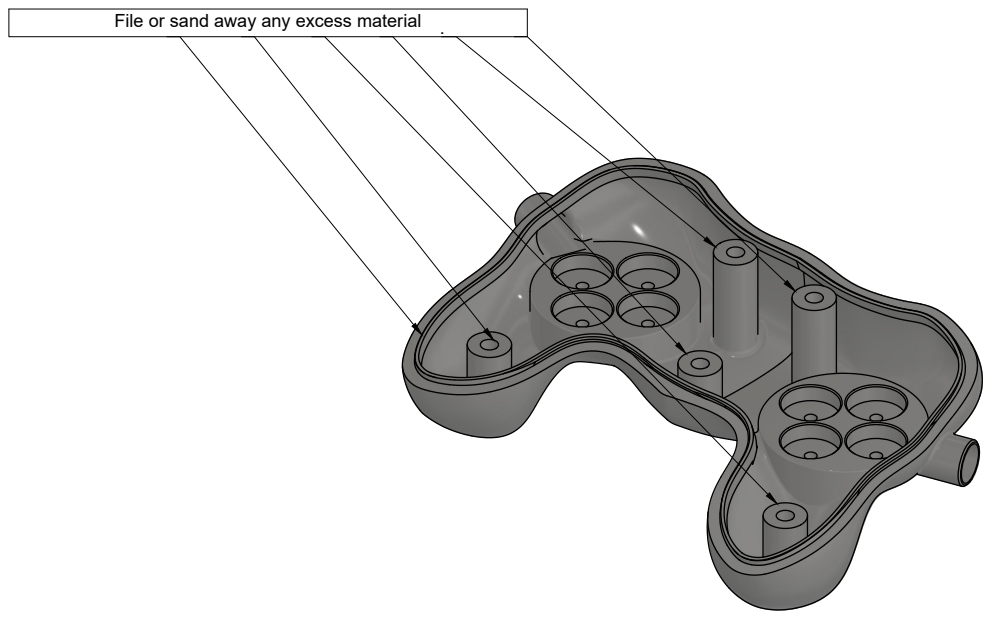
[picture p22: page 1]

File or sand away any excess material .

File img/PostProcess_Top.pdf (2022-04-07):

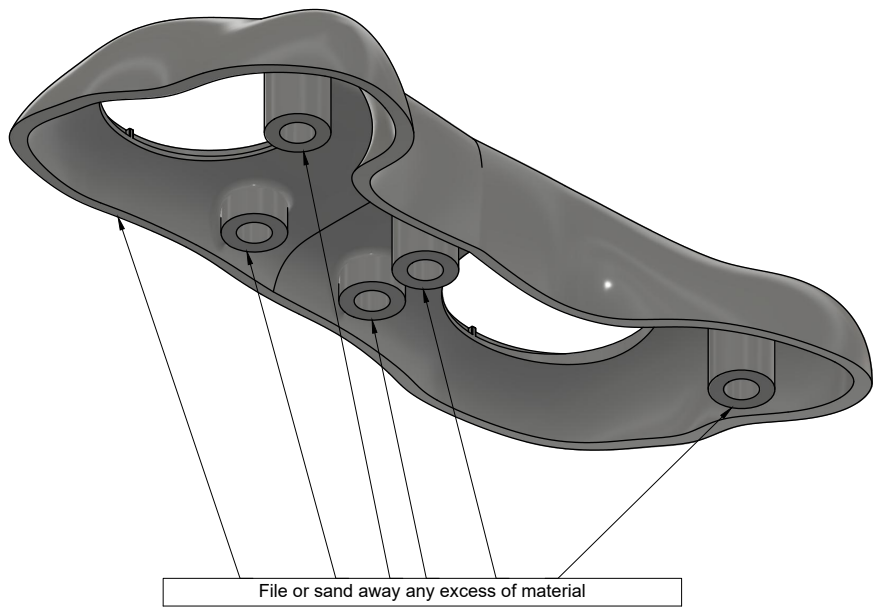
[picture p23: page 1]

File or sand away any excess of material

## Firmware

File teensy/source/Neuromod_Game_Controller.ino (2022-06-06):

/*
    Name:       Neuromod_Game_Controller.ino
    Created:	2019-01-08 11:22:35
    Author:     Andre Cyr
*/

#include <usb_keyboard.h>

char keyVal[] = {'A','B','X','Y','U','R','D','L'};
char trgKeyVal = '5';
uint8_t rxPin[] = { 24,25,26,27,28,29,30,31 };
uint8_t nPin = sizeof(rxPin);
uint16_t rxPinState[sizeof(rxPin)];
uint8_t trgPin = 2;
uint8_t txPin[] = {14,15,16,17,18,19,20,21,22,23};
uint16_t timeKeyPressed;
bool buttonPressed[sizeof(rxPin)];
bool buttonToggled[sizeof(rxPin)];
bool trigKeyPressed;
volatile bool triggered = false;
bool debug;
uint8_t ledPin = 13;
uint8_t trgKeyPressLength;

// The setup() function runs once each time the micro-controller starts
void setup()
{
	pinMode(trgPin, INPUT);
	pinMode(ledPin, OUTPUT);
	debug = digitalRead(trgPin) == 0 ? true : false;
	trgKeyPressLength = 10; // duration of key press for trigger in ms

	for (int i = 0;i < nPin;i++)
	{
		pinMode(rxPin[i], INPUT);
		rxPinState[i] = 0;
		buttonPressed[i] = true;
		buttonToggled[i] = true;
	}

	for (int i = 0; i < nPin; i++)
	{
		pinMode(txPin[i], OUTPUT);
		digitalWrite(txPin[i], HIGH);
	}

	attachInterrupt(trgPin, trgIn, RISING);

	delay(1000); //required for PC to properly detect keyboard

	Keyboard.println("Initializing...");
	Keyboard.print("Trigger key = ");
	Keyboard.println(trgKeyVal);
	for (int i = 0;i < nPin;i++)
	{
		bool pinDetected = digitalRead(rxPin[i]) ? false : true;
		if (pinDetected)
		{
			Keyboard.print("Key ");
			Keyboard.print(keyVal[i]);
			Keyboard.println(" : OK ");
		}
		else
		{
			Keyboard.print("Key ");
			Keyboard.print(keyVal[i]);
			Keyboard.println(" : not detected ");
		}
	}
}

// Add the main program code into the continuous loop() function
void loop()
{

	if (debug)
	{
		// write debug code here
		// debug mode is activated by pulling pin 2 (trigger pin) low at start-up


	}

	else
	{
		if (triggered)
		{
			Keyboard.press(trgKeyVal);
			timeKeyPressed = millis();
			trigKeyPressed = true;
			triggered = false;
		}
		else
		{
			if (trigKeyPressed)
			{
				if ((millis() - timeKeyPressed) > 10)
				{
					Keyboard.release(trgKeyVal);
					trigKeyPressed = false;
				}
			}
		}


		// Sequentially reads each key state and writes state as LSB in rxPinState[i]
		// shiftings bits left by 1 bit

		for (int i = 0;i < nPin;i++)
		{
			rxPinState[i] = (rxPinState[i] << 1) | (1 & digitalRead(rxPin[i]));
		}

		for (int i = 0;i < nPin;i++)
		{

			// The key state will be considered pressed and debounced if all bits are 1s,
			// or released and debounced if all bits are 0s (16 identical readings)

			if (rxPinState[i] & 65535)
			{
				buttonToggled[i] = buttonPressed[i] ? false : true;
				buttonPressed[i] = true;

			}
			if (!rxPinState[i])
			{
				buttonToggled[i] = buttonPressed[i] ? true : false;
				buttonPressed[i] = false;
			}
		}

		for (int i = 0;i < nPin;i++)
		{
			if (buttonPressed[i] & buttonToggled[i])
			{
				Keyboard.press(keyVal[i]);
				buttonToggled[i] = false;
			}
			if (!buttonPressed[i] & buttonToggled[i])
			{
				Keyboard.release(keyVal[i]);
				buttonToggled[i] = false;
			}
		}
	}
}

void trgIn()
{
	triggered = true;
}

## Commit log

2021-05-12 Bill of materials
2021-05-12 Added metric thread equivalence
2021-07-30 stl files
    Added shutter cap and blade stl
    Added shutter cap parametric
    [Shutter_Cap _parametric.f3d]
2021-08-03 source teensy
2021-08-04 PCB files
    [copper_bottom.gbr, copper_top.gbr, drills.xln, profile.gbr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]
2021-08-05 stl files
    Added models for interface enclosure
2022-01-17 add placeholders for switch assembly
2022-01-27 add shutter assembly pics
2022-01-27 shutter assembly procedure
2022-01-28 remove CAD file
    [Shutter_Cap _parametric.f3d]
2022-01-28 add oarametric shuter design
    [Shutter_Assembly_Param v1.f3d]
2022-01-28 fix broken link
    [Shutter_Assembly_Param.f3d]
2022-03-23 Added Fusion assembly file for the controller
2022-03-28 Move 3d print stuff to single file
2022-03-28 Casing_top printing info
2022-03-28 Casing_Bottom printing info
2022-03-28 Switch_Body print info
2022-03-28 change support material info in switch_body
2022-03-28 Shutter_Cap print info
2022-03-28 Shutter blade print info
2022-03-28 DPad support print info
2022-03-30 Comment on DPad support print settings
2022-03-30 Add printing info for Button support
2022-03-30 button support print info
2022-03-30 Add direction button print info
2022-03-30 Add Round button print info
2022-03-30 Add dpad cover and button cover print info
2022-03-31 cleaned up print info
2022-04-01 switch assembly
    [Shutter_Cap.step]
2022-04-01 PCB pic
2022-04-07 Assembly instructions - fit test
2022-05-30 PCB assemby
2022-06-06 PCB images
2022-06-06 |add gerber files
    [copper_bottom.gbr, copper_top.gbr, drills.xln, profile.gbr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]
2022-06-06 add PCB cad
2022-06-06 add PCB stp file
2022-08-25 moved structure up 1 level
    [Shutter_Assembly_Param.f3d, Shutter_Cap.step]
